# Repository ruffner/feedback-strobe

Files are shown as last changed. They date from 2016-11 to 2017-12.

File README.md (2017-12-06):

# Feedback Strobe

The Feedback Strobe is a technology demonstration aid for EE422G Signals and Systems Laboratory at the University of Kentucky. Commisioned by [Dr. Kevin Donohue](https://www.engr.uky.edu/research/researchers/kevin-donohue/) and [Dr. Michael Johnson](https://www.engr.uky.edu/research/researchers/michael-t-johnson/), the device facilitates hands on involvement in many aspects of a persistence of vision project. The students will be tasked with programming an ARM microcontroller using the Arduino IDE to control both rotation and blink speed of the device in order to produce a persistence of vision effect.

## Lab Procedure
### Setup
#### Basic tools, supplies
Gonna need some wire. Maybe some pliers for the wires that got tinned super heavy, these breadboards are tight. A bench power supply will be necessary after the all the connections have been made. 

When determining the rotation speed, an oscilloscope will probably be handy to for characterizing the output of the reflectance sensor.

#### IDE
A computer with a working install of the [Arduino IDE](https://www.arduino.cc/en/Main/Software) will also be necessary. For the PID part of the lab, a library will have to be installed. [Here](https://www.arduino.cc/en/Guide/Libraries) is a guide on how this is done.

#### Adding Teensy support
For the Arudino IDE to support cross compiling to the CortexM on the Teensy, Paul Stoffregen's [Teensyduino add-on](https://www.pjrc.com/teensy/teensyduino.html) must be downloaded and installed. All platforms are supported. Point the installer at your copy of the IDE and let it install the necessary tools. 
 
Now, in the *Tools > Board:* menu of the Arduino IDE, a 'Teensy 3.2 / 3.1' option will exist. Choose it. Now make sure you can see an available corresponding serial port in the *Tools > Port* menu. reset the Teensy if it doesn't show.

### LED and IR Sensor Setup
First, the leads of the LED must be mapped to [Teensy 3.2](https://www.sparkfun.com/products/13736) pin numbers. The Figure below shows the color coding of the slip ring wires. Make sure to connect the output of the reflectance sensor to a pin with ```analogRead()``` capabilities.

#### Parts and layout
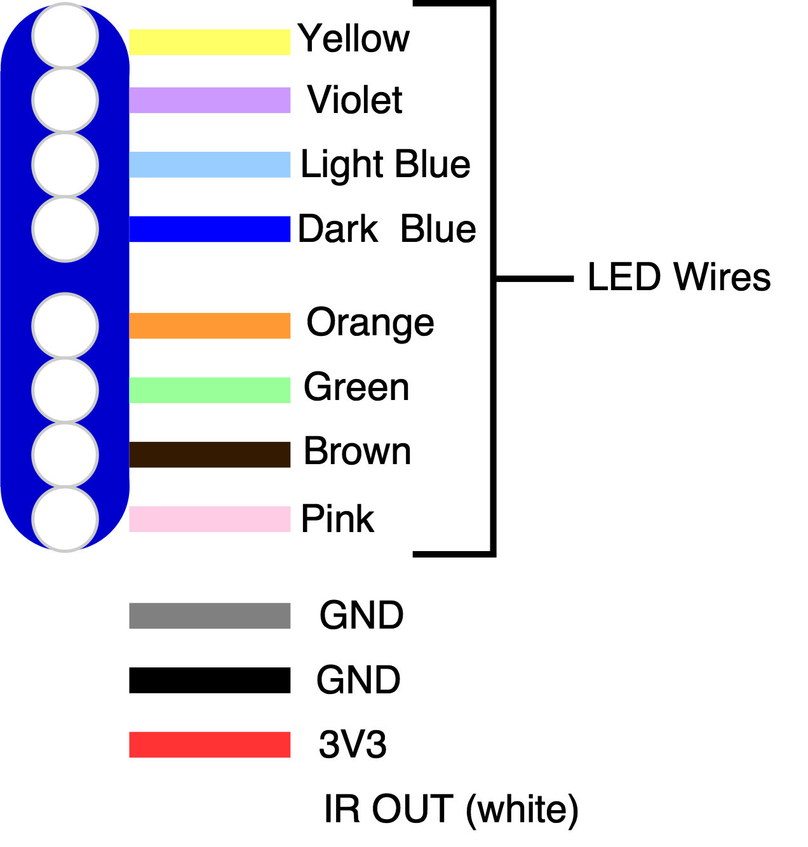
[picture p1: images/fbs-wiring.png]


There is an [analog reflectance sensor](https://www.sparkfun.com/products/9453) on the underside of the propellor who's signal (the white slip ring wire) varies upon rotation of the propellor. The white pulley on the motor shaft provides a high reflectance surface causing the output of the IR reflectance sensor to decrease. Thus, the analog signal will have local minima upon completion of a rotation.

Slip ring wires can be pinned under the Teensy upon insertion into the breadboard. This eases the breadboarding process. 

#### Teensy pinout
Any GPIO on the [Teensy pins](https://www.pjrc.com/teensy/card7a_rev1.png) can be used for driving the LEDs.

#### Powering the reflectance sensor
The IR reflectance sensor can be powered from the Teensy's onboard 3.3V regulator. It is *NOT* a 5V tolerant IC!

Make sure the reflectance sensor output voltage is least when over the drive pulley. Test that all of the LEDs can be turned both on and off.

### Back EMF Protection and Motor Circuit

The schematic below shows the ciruit to build to interface with the motor. The two thicker red (+) and blue(-) wires are not part of the slip ring 12, they are the motor wires. Connect the (-) to the drain of the MOSFET. 

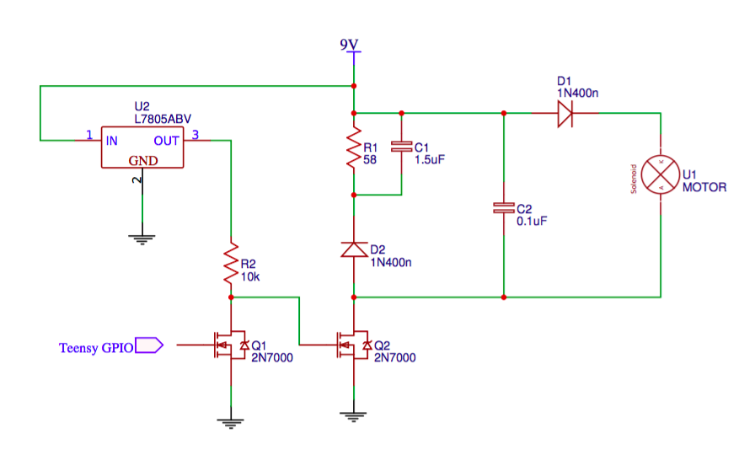
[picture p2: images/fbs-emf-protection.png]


Parts supplied to build this circuit are as follows:
 - 1x [STP60N N channel MOSFET](http://www.st.com/content/ccc/resource/technical/document/datasheet/95/a9/32/90/53/2f/44/4f/CD00154892.pdf/files/CD00154892.pdf/jcr:content/translations/en.CD00154892.pdf)
 - 1x [7805 5V Regulator](https://www.sparkfun.com/datasheets/Components/LM7805.pdf)
 - 1x [1N400x Diode](http://www.onsemi.com/pub/Collateral/1N4001-D.PDF) (Will have to find another in the lab.)
 - 1x 1.5 uF ceramic capacitor
 - 1x 0.1 uF ceramic capacitor
 - 1x 58 Ohm resistor
 - 1x 10 kOhm resistor
 
#### Power
The bench power supply should be set to 9 volts
 
The Teensy is powered from the ouput of the 5V regulator and should be attached to  *Vin* pin on the Teensy.

Make sure to common ground the bench supply and Teensy.

#### PWM Setup
Any pin on the Teensy shown with PWM capability may be used to drive the gate of the MOSFET.

Keep in mind the smallest PWM value will probably not be enough to break the stall torque of the motor, so a baseline minimum PWM that will start the motor will need to be establised.

### Programming Tasks
In order for the motor speed to track the blink rate, [PID controller](https://en.wikipedia.org/wiki/PID_controller) must be implemented. There is a handy [PID Library](https://playground.arduino.cc/Code/PIDLibrary) for this exact purpose, with helpful examples for setting up a basic plant. 

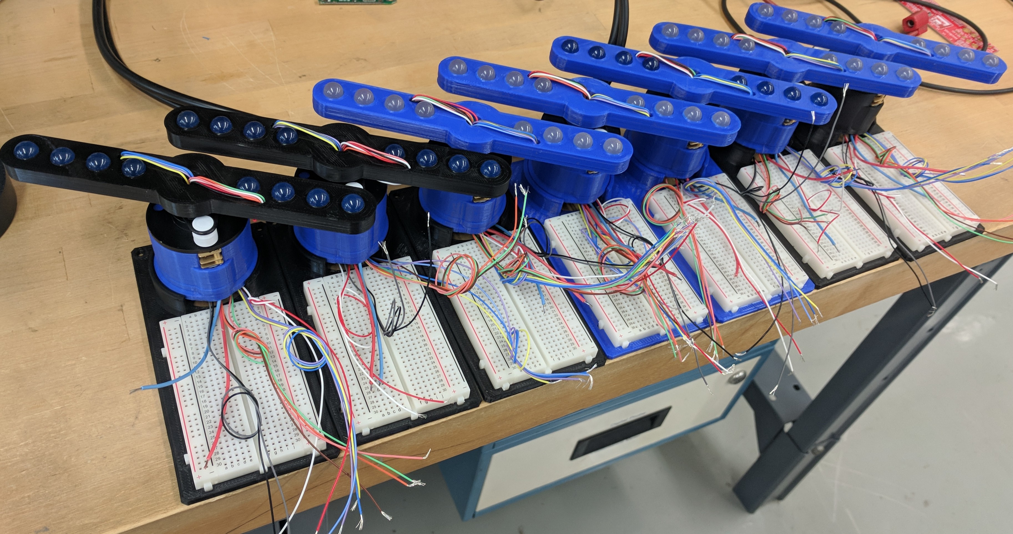
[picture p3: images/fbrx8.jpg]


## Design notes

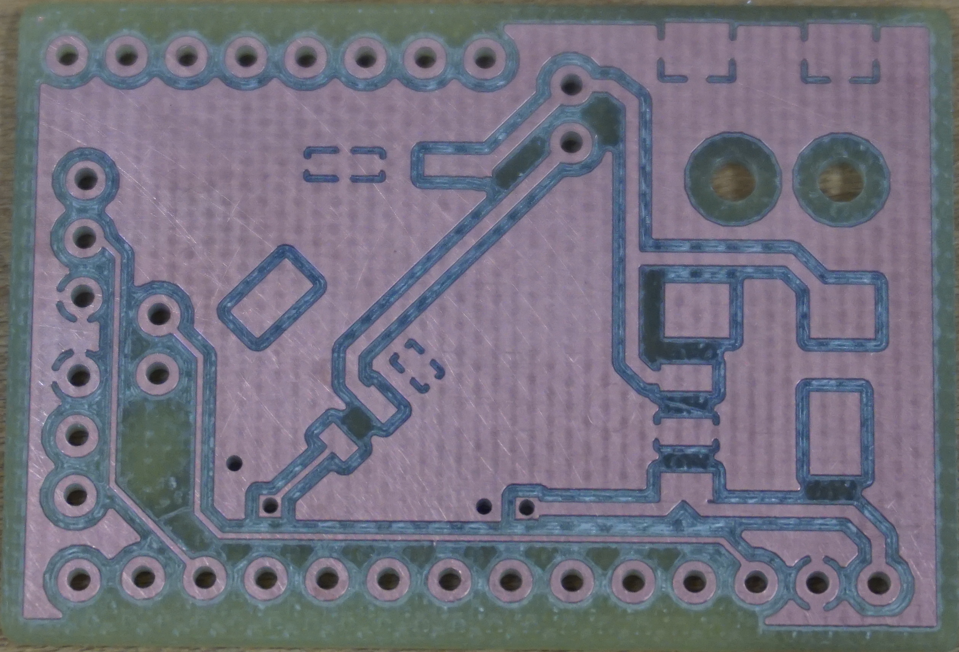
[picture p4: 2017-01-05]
images/v2pcb-top.jpg

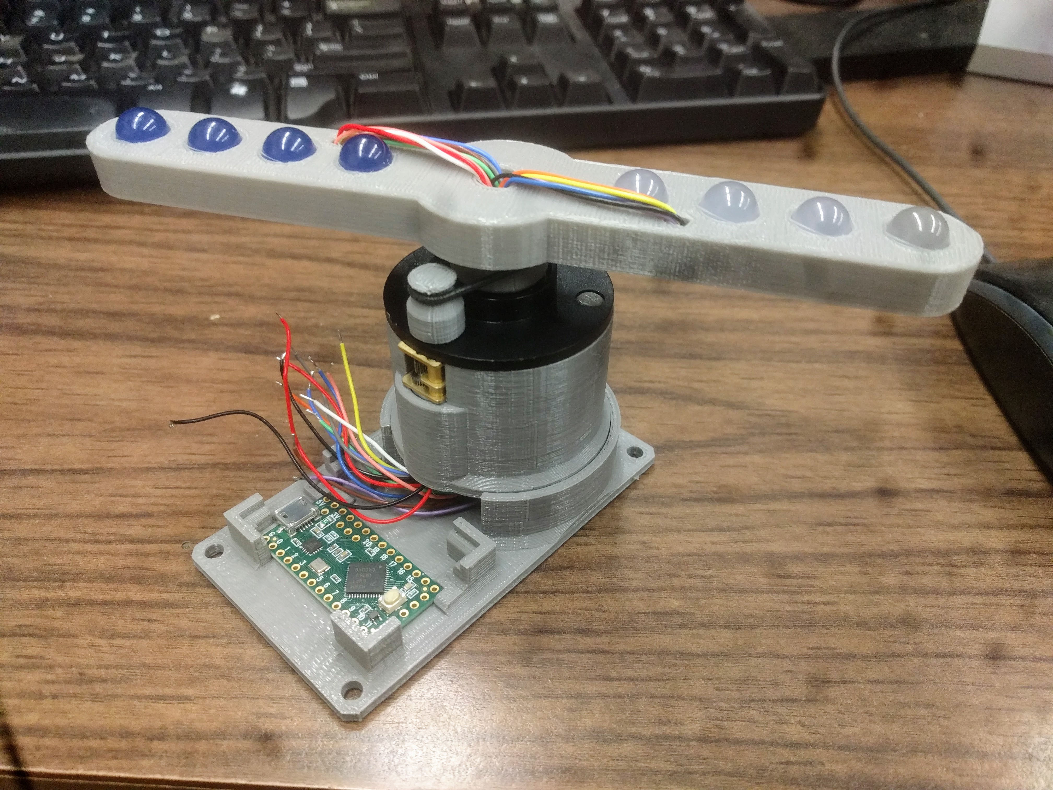
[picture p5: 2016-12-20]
images/v2body.jpg

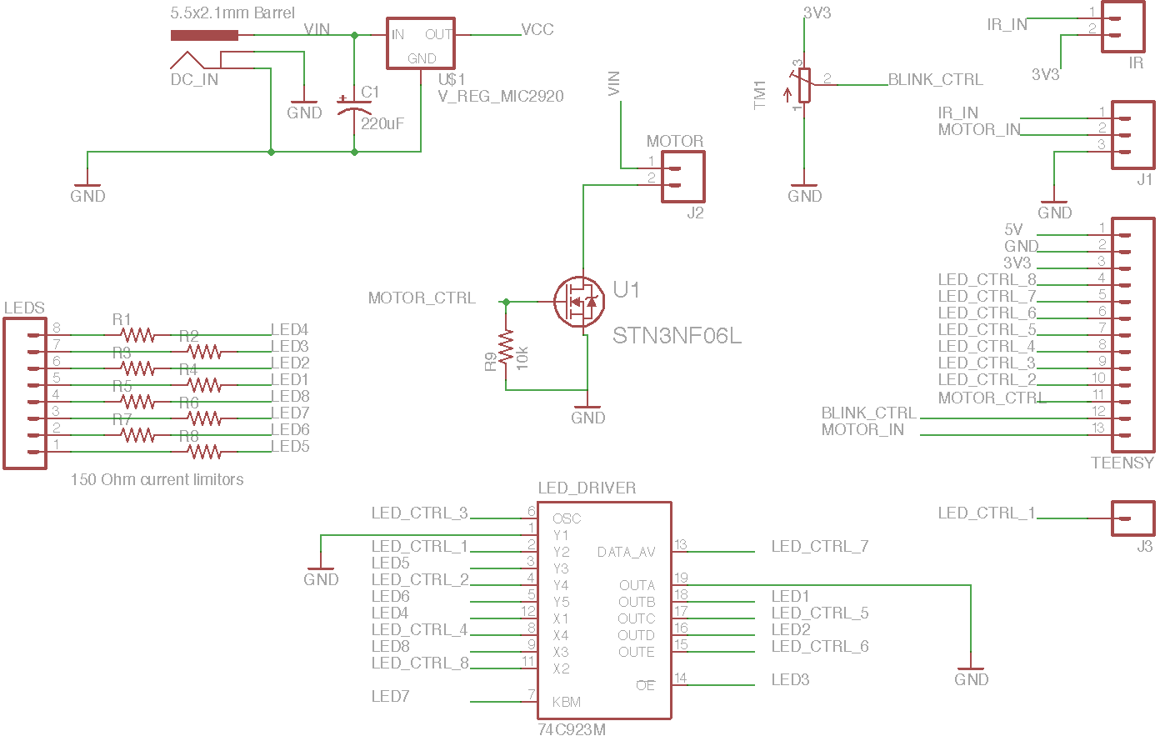
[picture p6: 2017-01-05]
images/v2pcb-sch.png

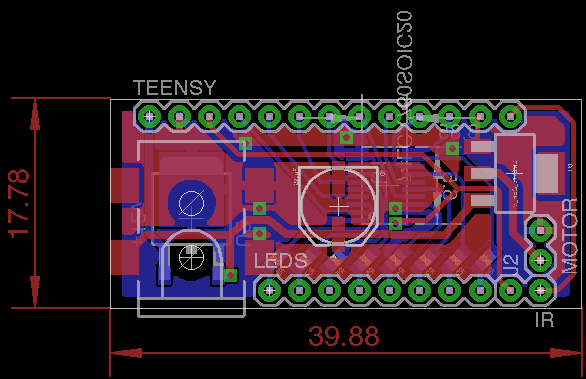
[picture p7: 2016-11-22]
images/v1pcb-brd.png

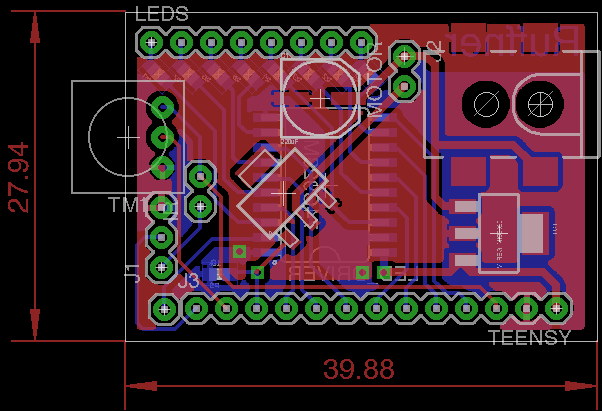
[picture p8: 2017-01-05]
images/v2pcb-brd.png

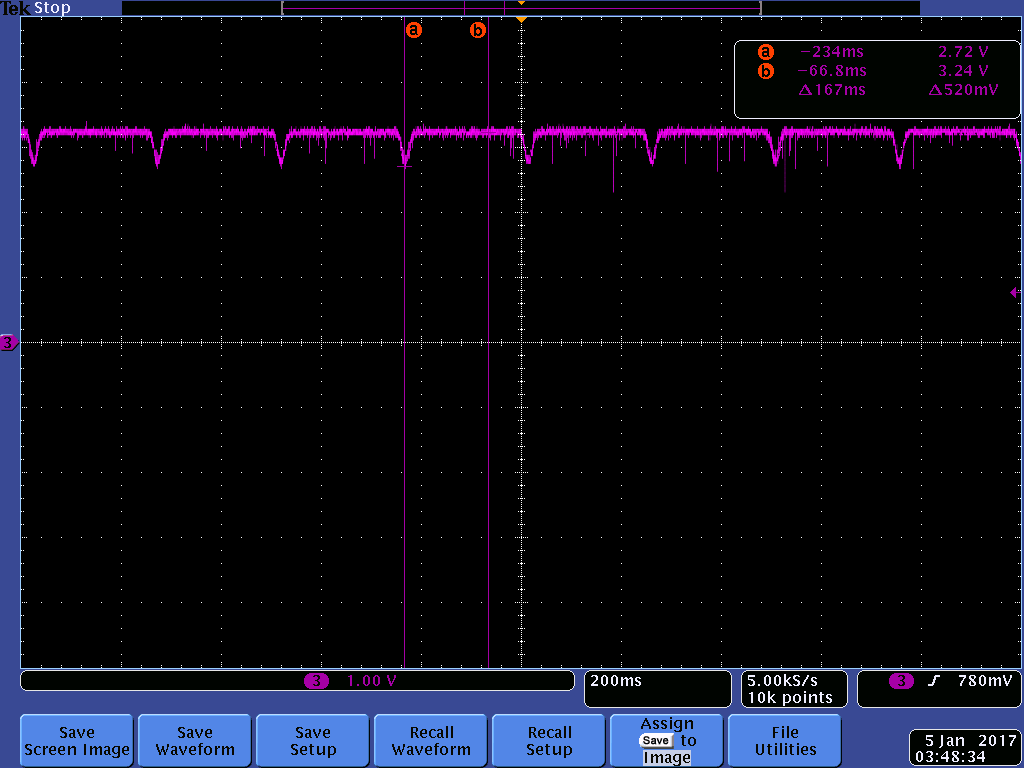
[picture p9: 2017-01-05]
images/scope-mag.png

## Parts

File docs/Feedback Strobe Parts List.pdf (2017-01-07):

Quantity | Product Name | Product Description | Product URL | Unit Price | Total Item Price
1 | SMD resistor | 10k Ohm | http://www.digikey.com/product-detail/en/yageo/RC0603JR-0710KL/311-10KGRDKR-ND/732594 | $0.10 | $0.10
8 | SMD resistor | 150 Ohm | http://www.digikey.com/product-detail/en/yageo/RC0603FR-07150RL/311-150HRCT-ND/729905 | $0.10 | $0.80
1 | SMD capacitor | 220uF 16V | http://www.digikey.com/product-detail/en/nichicon/UWT1C221MCL1GS/493-2179-1-ND/590154UWT1C221MCL1GS | $0.36 | $0.36
1 | LCX760 | 8 bit open drain buffer | http://www.digikey.com/product-detail/en/fairchild-semiconductor/74LCX760WM/74LCX760WM-ND/974077 | $0.75 | $0.75
1 | Wall Power Supply | 9V 1A | http://www.digikey.com/product-detail/en/triad-magnetics/WSU090-1300/237-1451-ND/3094977 | $8.93 | $8.93
1 | DC Barrel Jack | 5.5mm OD 2mm ID | http://www.digikey.com/product-detail/en/cui-inc/PJ-002AH-SMT-TR/CP-002AHPJCT-ND/669692 | $1.44 | $1.44
1 | 5v Regulator | 1A | http://www.digikey.com/product-detail/en/on-semiconductor/NCP1117ST50T3G/NCP1117ST50T3GOSCT-ND/1967217 | $0.46 | $0.46
1 | N Channel MOSFET | 60V 4A | http://www.digikey.com/product-detail/en/stmicroelectronics/STN3NF06L/497-3177-1-ND/654516 | $0.63 | $0.63
1 | Male Headers | | https://www.sparkfun.com/products/116 | $1.50 | $1.50
1 | Slip Ring | 12 wire 2A | https://www.sparkfun.com/products/13065 | $19.95 | $19.95
4 | White LED | 10mm | https://www.sparkfun.com/products/11121 | $0.50 | $2.00
4 | Blue LED | 10mm | https://www.sparkfun.com/products/10635 | $0.50 | $2.00
1 | Micro Gear Motor | 2600 RPM | https://www.sparkfun.com/products/12518 | $12.95 | $12.95
1 | TeensyLC | 48 MHz ARM MCU | https://www.sparkfun.com/products/13305 | $12.95 | $12.95
1 | IR Reflectance Sensor | | https://www.sparkfun.com/products/9453 | $2.95 | $2.95
1 | PLA Filament | 100g @ $48/.9kg | https://store.makerbot.com/filament/pla-large/ | $5.33 | $5.33
Total Price: | $73.10

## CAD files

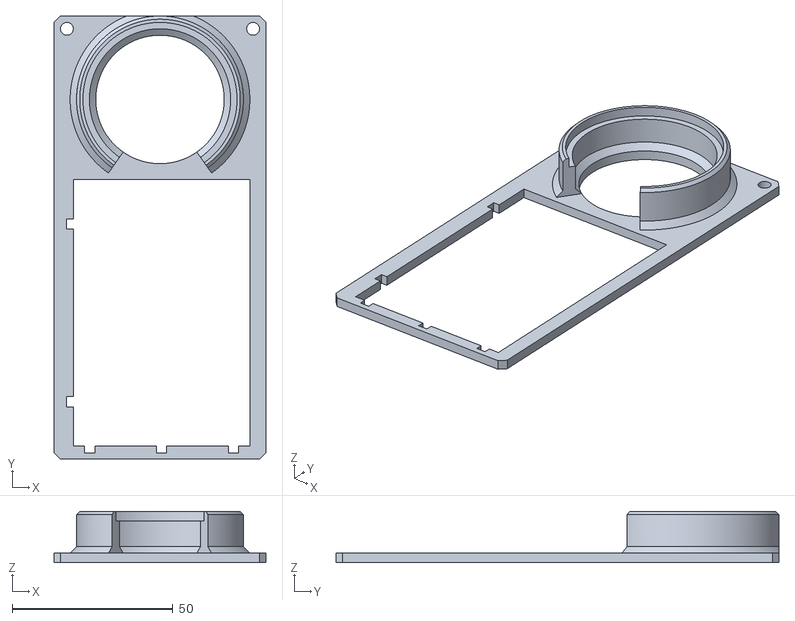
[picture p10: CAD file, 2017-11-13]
cad/stl/main-base.stl
66.0 x 138.0 x 16.0

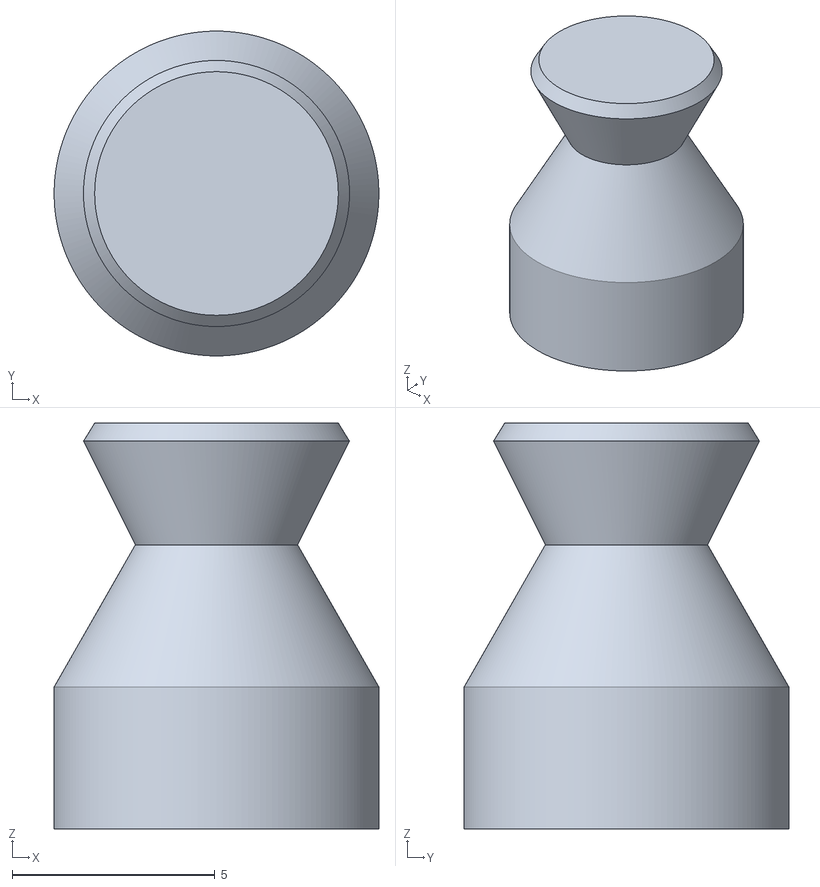
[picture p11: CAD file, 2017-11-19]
cad/stl/drive-pulley.stl
8.00 x 8.00 x 10.0

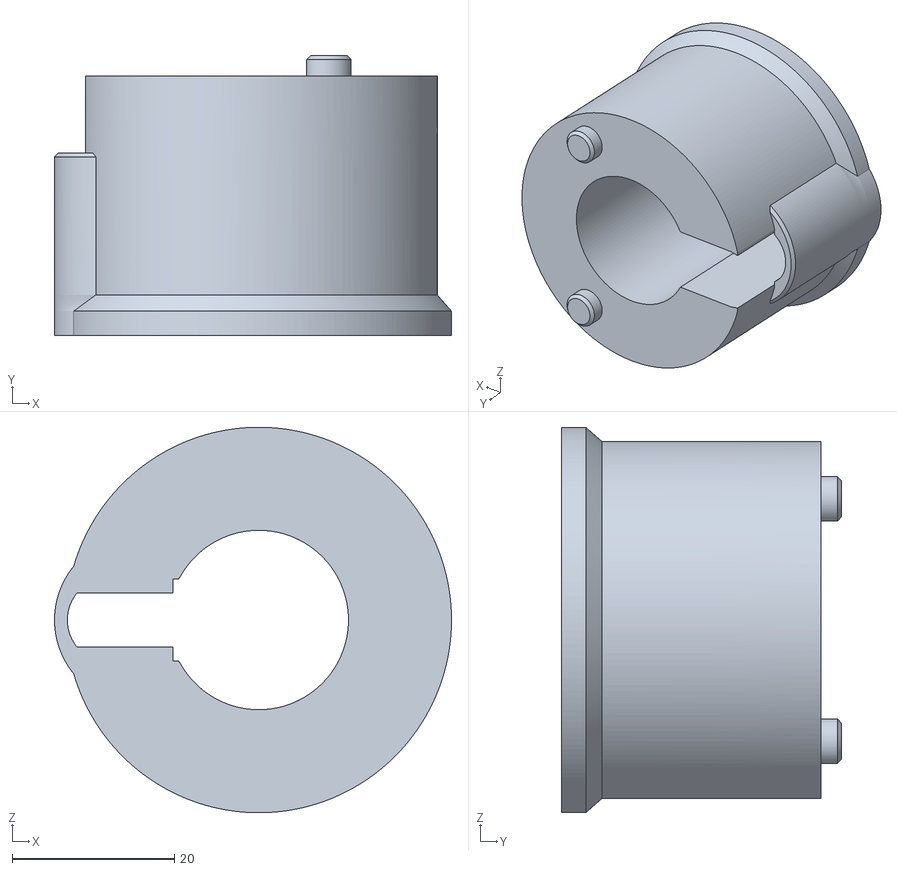
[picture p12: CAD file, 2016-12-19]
cad/stl/motor-mount.stl
48.9 x 34.5 x 47.5

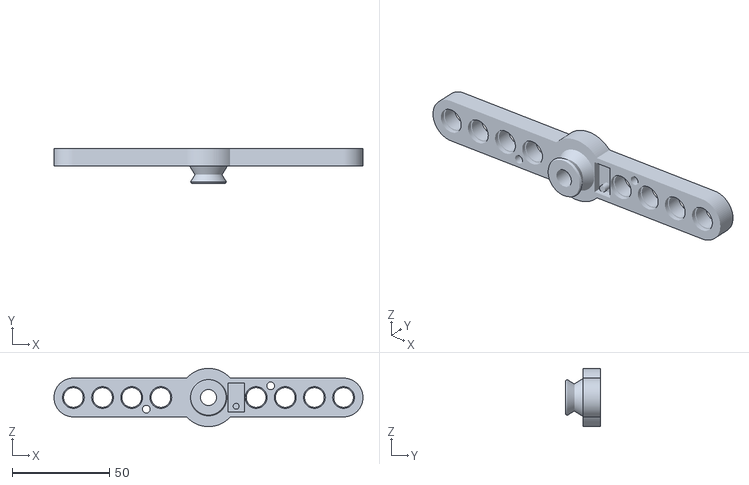
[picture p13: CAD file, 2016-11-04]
cad/stl/led-prop.stl
159.0 x 18.0 x 30.0

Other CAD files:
cad/drive-pulley.ipt
cad/led-prop.ipt
cad/main-base.ipt
cad/motor-mount.ipt
cad/shaft-adapter.ipt

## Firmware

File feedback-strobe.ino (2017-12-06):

// FEEDBACK STROBE V2 
// MATT RUFFNER 
// NOVEMBER 2017

#include <TimerOne.h>
#include <PID_v1.h>

//Define PID variables
double Setpoint, Input, Output;

// NUMBER OF LEDS
#define NLEDS 8

//Specify the links and initial tuning parameters
double Kp=.5, Ki=0, Kd=0;
PID myPID(&Input, &Output, &Setpoint, Kp, Ki, Kd, DIRECT);

/*------------------------------*/
/* HARDWARE CONNECTIONS         */
/*------------------------------*/
// INDIVIDUAL LED CONNECTIONS
#define LED1  12
#define LED2  11
#define LED3  10
#define LED4  9
#define LED5  17
#define LED6  16
#define LED7  15
#define LED8  14

// TO EASE ITERATIONS
const uint8_t leds[] = {LED1, LED2, LED3, LED4, LED5, LED6, LED7, LED8};

/* PWM SIGNAL TO MOSFET */
#define MOTOR_PIN 6

/* IR REFLECTANCE SENSOR ANALOG IN */
#define IR_PIN    23//A9
#define IR_SAMPLE_PERIOD 5000 // ISR PERIOD IN MICROSECONDS
#define IR_SAMPLE_COUNT 200
float irSamples[IR_SAMPLE_COUNT];
unsigned long irSampleIndex = 0;
volatile unsigned long lastIrMinTimestamp = 0;
volatile unsigned long lastRotationPeriod = 0;
float currentRotationFreq = 0;


// LED BLINK CONTROL VARIABLES
bool ledState = LOW;
unsigned long lastStrobeTime = 0; 
unsigned long strobeOffTime = 120; 
unsigned long strobeOnTime =  5;

double blinkFreq = 1.0 / ((strobeOnTime + strobeOffTime)/1000.0);

volatile bool started = 0;
volatile bool newFreq = 0;

#define DEBUG 1

void setup()
{
  Serial.begin(9600);
  
  // SET LEDS AS OUTPUTS AND TURN THEM OFF
  if( DEBUG ) Serial.println("Setting LEDs as outputs...");
  for (uint8_t i=0; i<NLEDS; i++ ){
    pinMode(leds[i], OUTPUT);
    digitalWrite(leds[i], LOW);
  }


  // SET MOTOR AS OUTPUT, TURN OFF
  if( DEBUG ) Serial.println("Initializing motor as output...");
  pinMode(MOTOR_PIN, OUTPUT);
  //driveMotor(255);


  // SET REFLECTANCE SENSOR AS INPUT
  if( DEBUG ) Serial.println("Setting up analog input sampling...");
  pinMode(IR_PIN, INPUT);
  Timer1.initialize(IR_SAMPLE_PERIOD);
  Timer1.attachInterrupt(sampleIRSensor);

  Serial.println("Setting PID variables");
  Input = currentRotationFreq;
  Setpoint = map(blinkFreq*10, 0, 150, 0, 2550)/10.0;
  myPID.SetOutputLimits(150,255);
  myPID.SetMode(AUTOMATIC);

  Serial.println("Starting...");

  driveMotor(200);
}

unsigned long lastFreqUpdate = 0;

void loop() 
{
  // put your main code here, to run repeatedly:

  if( millis() - 1000 > lastFreqUpdate ){

    noInterrupts();
    double t = currentRotationFreq;
    interrupts();
    
    Serial.print("current rot freq: ");
    Serial.println(t);
    lastFreqUpdate = millis();

    Input = map(t*10, 0, 150, 0, 2550)/10.0;

    myPID.Compute();
    
    Serial.print("new PID output: ");
    Serial.println(Output);

    driveMotor(Output);
  }

  
//  // UPDATE ROTATION SPEED
//  if( started && newFreq ){ 
//    noInterrupts();
//    Serial.print("rot freq: ");
//    Serial.println(currentRotationFreq);
//
//    
//    newFreq = 0;
//  }


  // drive LEDs
  if( millis() - lastStrobeTime > ( ledState ? strobeOnTime : strobeOffTime ) ){
    // update timestamp
    lastStrobeTime = millis();
    
    toggleStrobe();
  }

}

void sampleIRSensor()
{
  static bool state = 0;
  uint16_t n = (irSampleIndex++) % 200;
  irSamples[n] = (map(analogRead(IR_PIN), 0, 1023, 0, 10000)-5000)/10000.0;

  // with ir in from -0.5-0.5, dIr_dt can range from -50 to 50 
  if( irSampleIndex > 0 ){
    // derivative 2 most recent IR readings
    float dirdt = (irSamples[n]-irSamples[n-1]) / (IR_SAMPLE_PERIOD * 0.000001);
    unsigned long rn = millis();

    // trigger once a negative slope above a threshold is reached
    // when a positive dirdt is found it will be at the valley of the signal dip
    switch( state ){
    case 0:
      if( dirdt < -5 ){
        state = 1;
      }
      break;
    case 1:
      if( dirdt > 0 ){
        lastRotationPeriod = rn - lastIrMinTimestamp;
        lastIrMinTimestamp = rn;
        state = 0;
        currentRotationFreq = (float)(1000.0/lastRotationPeriod);
        //Serial.println(currentRotationFreq);
        if( !started ) started = 1;
        //newFreq = 1;
      }
    } 
  }
}

void toggleStrobe()
{
  uint8_t i;
  
  ledState = !ledState;

  for( i=0; i<NLEDS; i++ ){
    digitalWrite( leds[i], ledState );
  }
}

void driveMotor(uint8_t spd)
{
  uint8_t realSpeed = map(spd, 0, 255, 255, 0);
  analogWrite(MOTOR_PIN, realSpeed);
}

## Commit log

2016-10-30 first commit, first iteration of cad drawings and stls
    [main-base.ipt, main-base.stl, motor-mount.ipt, motor-mount.stl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]
2016-11-01 tweaked motor slot width, shaft adapter flatspot
    [main-base.ipt, main-base.stl, motor-mount.ipt, motor-mount.stl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]
2016-11-01 Created spinning LED arm with cutout for IR reflectance sensor. Testing to see if printed gear teeth will work.
    [led-prop.ipt, led-prop.stl]
2016-11-04 moved to pulley drive system. added drive pulley to fit on motor
    [drive-pulley.ipt, drive-pulley.stl, led-prop.ipt, led-prop.stl]
2016-11-07 updated drive pulley
    [drive-pulley.ipt, drive-pulley.stl]
2016-11-07 updated drive pulley shaft depth
    [drive-pulley.ipt, drive-pulley.stl]
2016-11-07 shortened drive pulley
    [drive-pulley.ipt, drive-pulley.stl]
2016-11-08 started on board layout
    [feedback-strobe.brd, feedback-strobe.sch]
2016-11-09 finished v1 PCB design
    [feedback-strobe.brd, feedback-strobe.sch]
2016-11-22 started on software, added images of v1 pcb layout
2016-11-22 edited mosfet label
    [feedback-strobe.brd, feedback-strobe.sch]
2016-11-25 added image of first assembly
2016-12-19 revised mounting base
    [main-base.ipt, main-base.stl]
2016-12-19 added motor securing structural support, revised board mount location, shortened pulley
    [drive-pulley.ipt, drive-pulley.stl, main-base.ipt, main-base.stl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]
2016-12-20 added data flow diagram and corresponding draw.io xml source
2016-12-29 new components added, new board dimensions set. routing started. mosfet footprint from digikey not wanting to connect nets
    [feedback-strobe.brd, feedback-strobe.sch]
2016-12-29 initial completion of v2 pcb design
    [feedback-strobe.brd]
2016-12-29 added dimensions
    [feedback-strobe.brd]
2017-01-04 shifted teensy mounting location on main base part design. added chamfer to top rim.
    [main-base.ipt, main-base.stl]
2017-01-05 added new voltage regulator, reduced number of vias, added more spacing between traces.
    [feedback-strobe.brd, feedback-strobe.sch]
2017-01-05 updated pin defs for v2 board
2017-01-05 put my name on the board
    [feedback-strobe.brd]
2017-01-05 added images of new pcb and finished build
2017-01-05 updated data flow diagram
2017-01-05 added v2.1 pcb images
2017-01-06 strobe rate and motor speed controlled by analog inputs, yet to be tested
2017-01-06 specified voltage range on adc pin
2017-11-13 redesigned mainbase to hold breadboard for lab assembly
    [main-base.ipt, main-base.stl]
2017-11-15 increased shaft size in drive pulley
    [drive-pulley.ipt, drive-pulley.stl]
2017-11-23 added wiring diagram for prop
2017-11-23 updated wiring image
2017-11-24 updated emf protection circuit
2017-11-27 updated emf schematic to include 5v reg
2018-08-12 removed old files
    [feedback-strobe.brd, feedback-strobe.sch]
